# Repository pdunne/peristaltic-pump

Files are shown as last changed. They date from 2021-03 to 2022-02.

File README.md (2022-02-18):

# peristaltic-pump

Arduino code and electronics design for a simple peristaltic pump.

- Use a toggle switch to change between off, forward, and reverse flow
- A potentiometer to vary the rotation rate of the DC motor.
- Output the rotation direction and rotation rate as calibrated flow rate on a 128x64 OLED
- Can control two pumps simultaneously

## Getting Started

1. Wire all elements as shown in the diagram.
2. Ensure you have a recent version of the Adafruit SSD1306 library.
3. Use [I2C scanner](https://playground.arduino.cc/Main/I2cScanner/) to detect
the I2C address of your OLED (e.g. `0x3C`), and input it into the following line:
`display.begin(SSD1306_SWITCHCAPVCC, 0x3C);`
4. Compile and upload the program to your Arduino compatible board

> :warning: **WARNING: If you are using an old Adafruit library (before Nov. 2018)**:
> Find Adafruit_SSD1306.h under the Arduino libraries:
>
> `PATH_TO_ARDUINO_INSTALLATION/libraries/Adafruit_SSD1306/`
>
> Look for  `SSD1306 Displays` and uncomment one define to match your display:
>
> e.g. uncomment only `#define SSD1306_128_64` if using a 128x64 OLED
> That section of the file should look like:
>
>  ``` c
>/*=========================================================================
>    SSD1306 Displays
>    -----------------------------------------------------------------------
>    The driver is used in multiple displays (128x64, 128x32, etc.).
>    Select the appropriate display below to create an appropriately
>    sized framebuffer, etc.
>
>    SSD1306_128_64  128x64 pixel display
>
>    SSD1306_128_32  128x32 pixel display
>
>    SSD1306_96_16
>
>    -----------------------------------------------------------------------*/
>     #define SSD1306_128_64
>//   #define SSD1306_128_32
>//   #define SSD1306_96_16
>/*=========================================================================*/
> ```
>
> Additionally, in `pump_control.ino` you might need to comment out the following
> line:
>
> `Adafruit_SSD1306 display(SCREEN_WIDTH, SCREEN_HEIGHT, &Wire, OLED_RESET);`

## Needed Material

1. Arduino compatible board (Uno rev. 3 used for this example)
2. LM2596 DC-DC step down module
3. 12 V power adapter
4. DC barrel socket power jack
5. OLED 128x64 I2C Monochrome Display
6. Low powered peristaltic pump using 12 V DC motor
7. L293D H-Bridge motor driver
8. Rotary Potentiometer (e.g. 10 kΩ)
9. Single Pull Single Throw Toggle Switch (On-Off-On)

## Wiring Guide

bread board

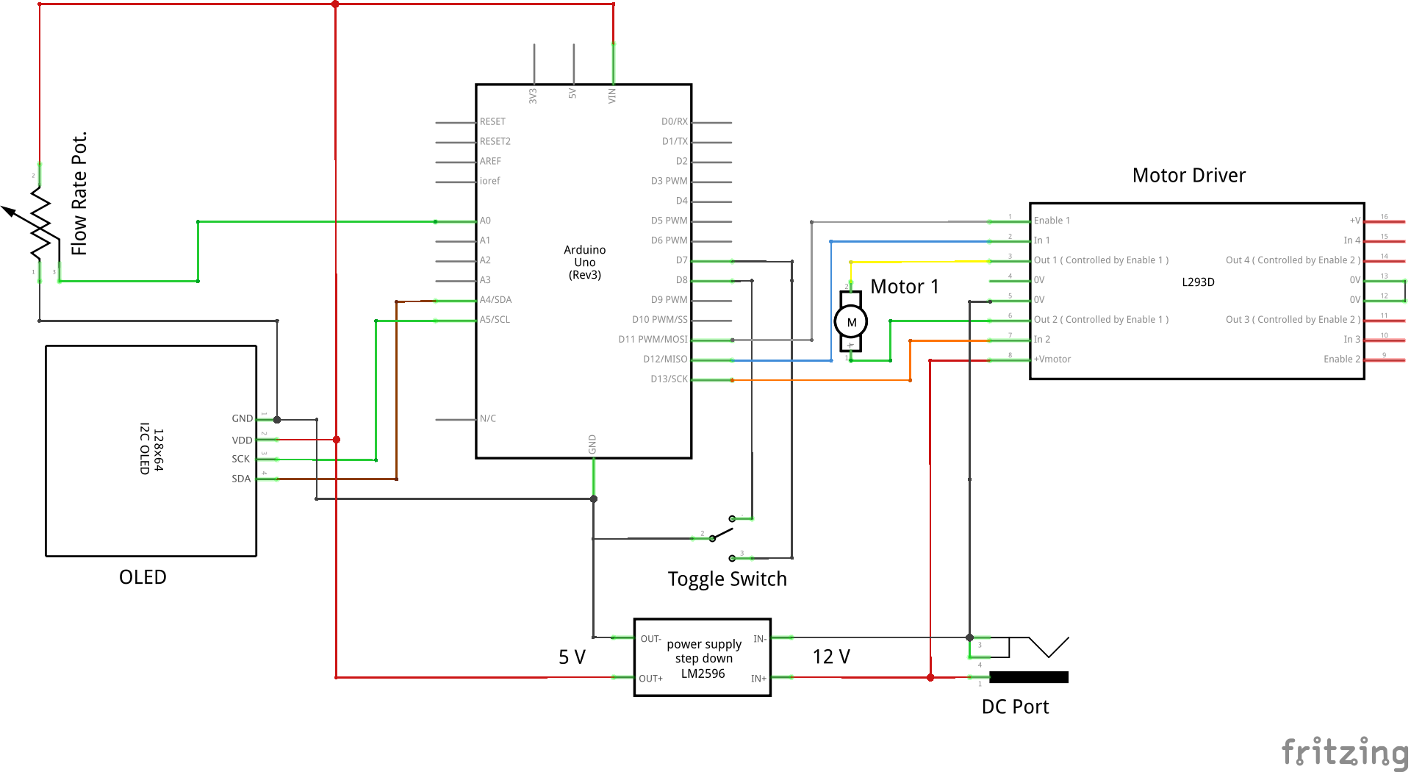
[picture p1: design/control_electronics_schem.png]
schematic


### Powering the Device

Assuming a 12 V DC adapter is used to power everything, it is convenient to place
a DC socket as the entry point to the device.
This be wired in two directions, the 12 V core to pin 8 of the L293D motor driver,
and to the high input of an LM2596 DC-DC step down converter. Similarly, the
ground can be connected to pin 3 of the L293D and the low input of the LM2596.
Adjust the DC-DC converter to produce 5 V across the output pins, which will be used
to drive the Arduino and OLED.

### Powering the Motor

We use control the motor in full H-bridge mode to be able to reverse the rotation
direction. Do this by connecting the following pins on the L293D motor driver:

| L293D              | Arduino/DC Jack     |
| ------------------ | ------------------- |
| Pin 1 (Enable)     | D11 PWM             |
| Pin 2 (In 1)       | D12                 |
| Pin 3 (Out 1)      | Motor pin 2         |
| Pin 4 (0 V )       | --                  |
| Pin 5 (0 V)        | Ground from DC Jack |
| Pin 6 (Out 2)      | Motor pin 1         |
| Pin 7 (In 2)       | D13                 |
| Pin 8 (+Vmotor)    | 12 V from DC Jack   |
| Pin 12 or 13 (0 V) | Ground from DC Jack |

Pins 2 and 7 determine the rotation state of the motor:

| Pin 2 | Pin 7 | Motor   |
| ----- | ----- | ------- |
| High  | Low   | Forward |
| Low   | High  | Reverse |
| High  | High  | Brake   |
| Low   | Low   | Brake   |

Pin 1 (Enable) is used to turn the motor, and regardless of pins 2 and 7, if Pin 1
(Enable) is low, then the motor will not rotate. Changing the rotation rate of the
motor is done using a PWM signal into Pin 1. This is sent as a duty cycle (% of
time on versus total time) as an int from 0 to 255 where 0%, i.e.  no pulses, and 255
means 100%, i.e. constant HIGH.

The function used to rotate the motor forward:

``` c
// Drives the motor forward at duty cycle 'duty_cycle'
void motor_forward(byte duty_cycle)
{
  display.println("Forward");
  digitalWrite(in1, HIGH);
  digitalWrite(in2, LOW);
  analogWrite(enable_motor_A, duty_cycle);
}
```

### Toggle Switch

The motor can be in one of three states, stopped, rotating forward, rotating reverse

Pins 7 and 8 are used for detecting the direction of a toggle switch (SPDT On-Off-On).
The two `On` poles of the switch are connected to pins 7 & 8, and the central pole
is connected to ground.

``` c
// Switch pins
const byte fwd_pin = 7; // Forward
const byte rev_pin = 8; // Reverse
```

We make sure the pins' internal pullup resistors are enabled to drive them to HIGH

```c
// Pins for Detecting Forward or Reverse
pinMode(fwd_pin, INPUT_PULLUP);
pinMode(rev_pin, INPUT_PULLUP);
```

Then whenever the toggle switch is enabled, this will ground one of the pins to LOW.
We detect the pin state with the following function, and then rotate or stop the
motor.

``` c
// Logic to check motor switch state
void motor_check()
{
  display.setCursor(0, 40);

  if (digitalRead(fwd_pin) == LOW)
  {
    motor_forward(duty_cycle);
  }
  else if (digitalRead(rev_pin) == LOW)
  {
    motor_reverse(duty_cycle);
  }
  else
  {
    motor_stop();
  }
}
```

### Flow Rate

The flow rate is set by reading the potential at pin `A0`,

`pot_value = analogRead(pot_read_pin);`

and mapping this to a value between 210-255. Lower than 210 stalls my motor

`duty_cycle = map(pot_value, 0, 1023, 210, 255);`

and for display on the OLED, the duty cycle is converted to flow rate calibrated
for this pump

```c
flow_rate = conv_flow_rate(duty_cycle);
```

The calibration was done using a third order polynomial, a balance between acurracy
and speed

```c
// Convert PWM values to flow rate. Only valid for forward flow, not reverse.
float conv_flow_rate(byte duty_cycle)
{
  // const float slope = 0.8073;
  // const float offset = -138.688;
  // float flow_rate = duty_cycle * slope + offset;

  // Third order polynomial.
  // Table lookup would be more efficient, but not needed
  const float a = -1.70373460e-04;
  const float b = 1.19023534e-01;
  const float c = -2.68600744e+01;
  const float d = 2.00133906e+03;
  float flow_rate = a * duty_cycle * duty_cycle * duty_cycle + b * duty_cycle * duty_cycle + c * duty_cycle + d;
  return flow_rate;
}
```

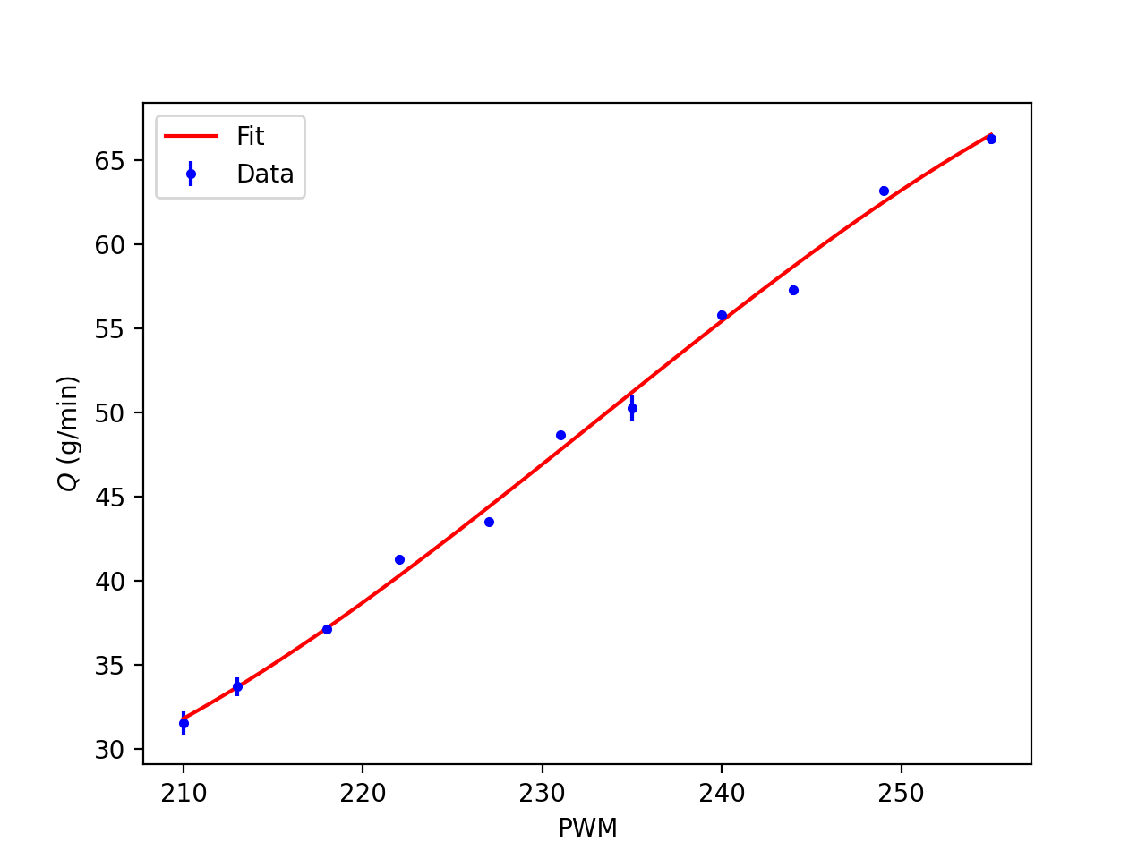
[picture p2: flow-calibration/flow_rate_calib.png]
calibration curve


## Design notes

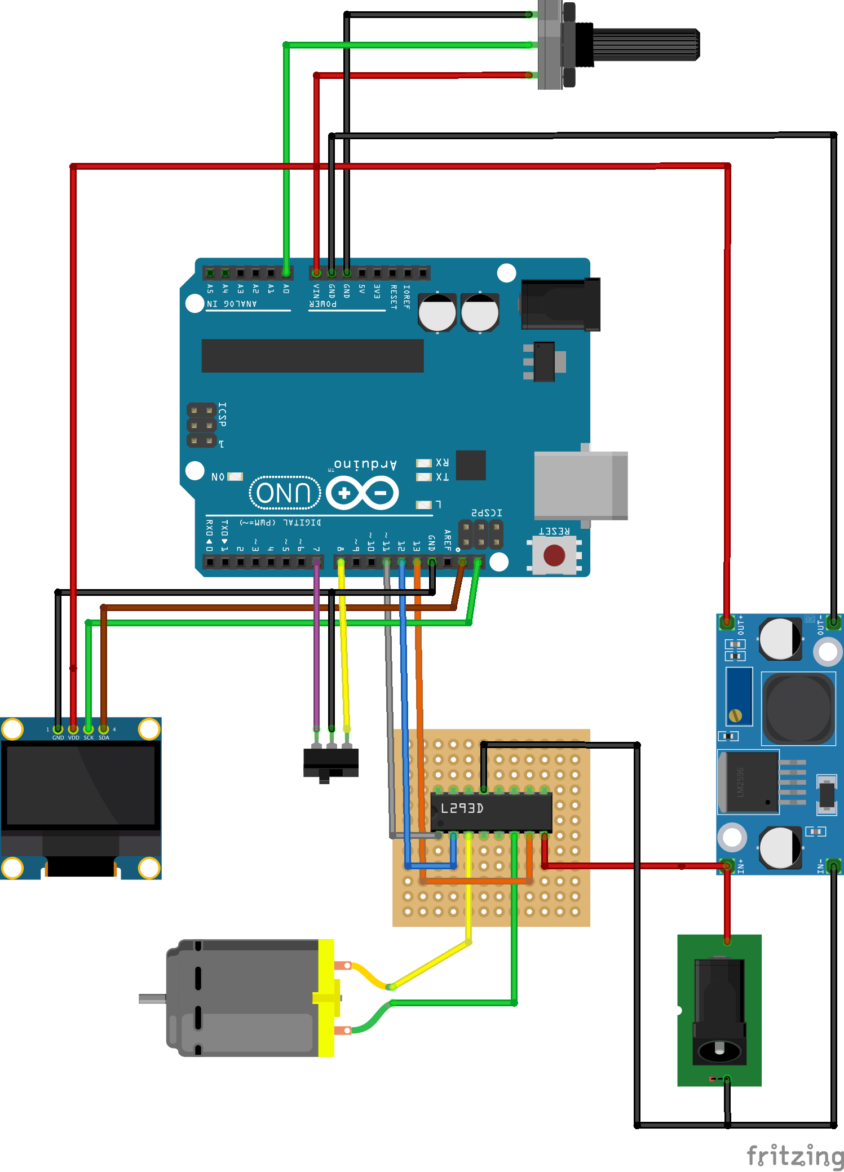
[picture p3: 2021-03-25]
design/control_electronics_bb.png

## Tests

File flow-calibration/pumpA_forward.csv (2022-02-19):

Duty Cycle | Flow | STD
100 | 72.77 | 0.174814187
90 | 67.4175 | 0.249537071
80 | 61.632 | 0.109799818
40 | 46.38 | 0.239930546
20 | 40.788 | 0.102254584
0 | 33.832 | 0.224267697

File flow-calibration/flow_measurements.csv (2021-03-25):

Dial | PWM | Run 1 | Run 2 | Run 3 | Run 4 | Run 5
0.0 | 210 | 29.276 | 30.750 | 31.311 | 31.880 | 32.340
0.5 | 213 | 32.569 | 32.906 | 33.880 | 34.097 | 33.997
1.0 | 218 | 34.444 | 37.031 | 36.854 | 37.268 | 37.479
1.5 | 222 | 41.044 | 41.140 | 41.052 | 41.264 | 41.697
2.0 | 227 | 42.368 | 43.372 | 43.759 | 43.458 | 43.476
2.5 | 231 | 48.790 | 48.511 | 48.486 | 48.824 | 48.823
3.0 | 235 | 49.093 | 50.091 | 50.013 | 49.673 | 51.343
3.5 | 240 | 56.028 | 55.395 | 55.812 | 55.972 | 55.943
4.0 | 244 | 56.519 | 57.570 | 57.165 | 56.925 | 57.457
4.5 | 249 | 63.440 | 63.283 | 63.025 | 63.467 | 62.915
5.0 | 255 | 65.555 | 66.437 | 66.642 | 65.954 | 66.056

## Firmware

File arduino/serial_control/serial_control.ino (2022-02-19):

/* This Source Code Form is subject to the terms of the Mozilla Public
 * License, v. 2.0. If a copy of the MPL was not distributed with this
 * file, You can obtain one at https://mozilla.org/MPL/2.0/.
 * Copyright 2022 Peter Dunne
 */

/*
Peristaltic Pump Control

Serial control of two DC pumps simultaneously.
Output the rotation direction and rotation rate as calibrated flow rate on a
128x64 OLED

Updated Feb 2022
By Peter Dunne

https://www.applied-magnetism.com/
https://github.com/pdunne/peristaltic-pump
*/

#include <SPI.h>
#include <Wire.h>
#include <Adafruit_SSD1306.h>

#define SCREEN_WIDTH 128 // OLED display width, in pixels
#define SCREEN_HEIGHT 64 // OLED display height, in pixels

// Declaration for an SSD1306 display connected to I2C (SDA, SCL pins)
#define OLED_RESET -1 // Reset pin # (or -1 if sharing Arduino reset pin)

/* New way to define screen properties with SSD1306 library. Might need to be
commented out for older versions of header. */
Adafruit_SSD1306 display(SCREEN_WIDTH, SCREEN_HEIGHT, &Wire, OLED_RESET);

const int loop_delay = 100; // Loop delay in ms

// Defines control pins, and min and max PWM values for a DC motor
struct Motor
{
  byte enable; // Enable motor (Digital pin)
  byte pin1;   // Input 1 (Digital pin)
  byte pin2;   // Input 2 (Digital pin)
  byte minPWM; // Minimum PWM duty cycle
  byte maxPWM; // Maximum PWM duty cycle
  byte id;     // Pump ID
};

// Defines forward and reverse detection pins
struct Control
{
  const byte fwd; // Forward Pin (Digital)
  const byte rev; // Reverse Pin (Digital)
  const byte pot; // Potentiometer Pin (Analog)
  byte flag;      // Status flag 0 - off, 1 - forward, 2 - reverse
};

// Stores potentiometer reading, duty cycle %, and calibrated flow rate in l/min
struct Flow
{
  int potVal;     // Potentiometer value
  byte dutyCycle; // Mapped duty cycle
  float flowRate; // Flow rate in l/min
};

typedef struct Motor Motor;
typedef struct Control Control;
typedef struct Flow Flow;

// Motor connections on H-Bridge
Motor motA = {11, 12, 13, 170, 255, 0};
Motor motB = {5, 4, 2, 180, 255, 1};

// Direction control pins
Control controlA = {7, 8, 0, 0};
Control controlB = {0, 1, 1, 0};

Flow flowA = {0, 0, 0.0};
Flow flowB = {0, 0, 0.0};

/******************************************/

// Function Prototypes
void setup(void);
void loop(void);
void init_switch(Control *control);
void init_motor(const Motor *motor);
void off_motor(const Motor *motor);
void motor_stop(const Motor *motor);
void motor_forward(const Motor *motor, byte dutyCycle);
void motor_reverse(const Motor *motor, byte dutyCycle);
void motor_check(const Motor *motor, Control *control, byte dutyCycle);
void init_display(byte dutyCycle);
void print_flow_rate(float flow_rate);
float conv_flow_rate(byte dutyCycle);
void control_flow(Motor *motor, Control *control, Flow *flow);

/******************************************/

// Setup board
void setup()
{
  // Set all the motor control pins to outputs
  init_motor(&motA);
  init_motor(&motB);

  // Turn off motor - Initial state
  off_motor(&motA);
  off_motor(&motB);

  // Pins for Detecting Forward or Reverse
  init_switch(&controlA);
  init_switch(&controlB);

  // Serial.begin(9600);
  // Set the address of the OLED
  display.begin(SSD1306_SWITCHCAPVCC, 0x3C);

  // Clear the buffer.
  display.clearDisplay();

  // Display Text
  display.setTextSize(3);
  display.setTextColor(WHITE);
  display.setCursor(0, 0);

  display.display();
  display.clearDisplay();
}
/******************************************/

// Detection of pins and control of pumps
void loop()
{
  // Reads potentiometer and sets the flow rate
  control_flow(&motA, &controlA, &flowA);
  control_flow(&motB, &controlB, &flowB);

  // Initialise display
  init_display(flowA.dutyCycle);

  // Check motor and display status
  display.setCursor(0, 40);

  motor_check(&motA, &controlA, flowA.dutyCycle);
  // display.setCursor(20, 40);
  motor_check(&motB, &controlB, flowB.dutyCycle);

  // Display Flow rate
  // print_flow_rate(flowA.flowRate);
  // print_flow_rate(flowB.flowRate);

  display.display();
  delay(loop_delay);
}

// Initialises pullup pins for switch detection
void init_switch(Control *control)
{
  pinMode(control->fwd, INPUT_PULLUP);
  pinMode(control->rev, INPUT_PULLUP);
}

// Intialises pins for controlling a motor
void init_motor(const Motor *motor)
{
  pinMode(motor->enable, OUTPUT);
  pinMode(motor->pin1, OUTPUT);
  pinMode(motor->pin2, OUTPUT);
  digitalWrite(motor->enable, LOW);
}

// Turns off a motor
void off_motor(const Motor *motor)
{
  digitalWrite(motor->pin1, LOW);
  digitalWrite(motor->pin2, LOW);
  analogWrite(motor->enable, 0);
}

// Turns off a motor
void motor_stop(const Motor *motor)
{
  display.println("Off");
  off_motor(motor);
}

// Drives the motor forward at duty cycle 'dutyCycle'
void motor_forward(const Motor *motor, byte dutyCycle)
{
  display.println("Forward");
  digitalWrite(motor->pin1, HIGH);
  digitalWrite(motor->pin2, LOW);
  analogWrite(motor->enable, dutyCycle);
}

// Drives the motor in reverse at duty cycle 'dutyCycle'
void motor_reverse(const Motor *motor, byte dutyCycle)
{
  display.println("Reverse");
  digitalWrite(motor->pin1, LOW);
  digitalWrite(motor->pin2, HIGH);
  analogWrite(motor->enable, dutyCycle);
}

// Logic to check motor switch state
void motor_check(const Motor *motor, Control *control, byte dutyCycle)
{

  if (digitalRead(control->fwd) == LOW)
  {
    control->flag = 1;
    motor_forward(motor, dutyCycle);
  }
  else if (digitalRead(control->rev) == LOW)
  {
    control->flag = 2;
    motor_reverse(motor, dutyCycle);
  }
  else
  {
    control->flag = 0;
    motor_stop(motor);
  }
}

// Initialise display
void init_display(byte dutyCycle)
{
  display.clearDisplay();
  display.setTextColor(WHITE);
  display.setCursor(0, 0);
  display.setTextSize(1);
  display.print("Motor:");
  display.setCursor(64, 0);
  display.println("Flow Rate:");
  display.setTextSize(2);
  // display.print(map(dutyCycle, min_PWM, max_PWM, 0, 100), DEC);
  display.print(flowA.dutyCycle);
  display.print(flowB.dutyCycle);

  // display.println("%");
}

// Display flow rate on OLED
void print_flow_rate(float flow_rate)
{
  display.setCursor(64, 8);
  display.println(flow_rate, 1);
  display.setCursor(64, 24);
  display.print("ml/mn");
}

// Convert PWM values to flow rate. Only valid for forward flow, not reverse.
float conv_flow_rate(byte dutyCycle)
{
  // const float slope = 0.8073;
  // const float offset = -138.688;
  // float flow_rate = dutyCycle * slope + offset;

  // Third order polynomial.
  // Table lookup would be more efficient, but not needed
  const float a = -1.70373460e-04;
  const float b = 1.19023534e-01;
  const float c = -2.68600744e+01;
  const float d = 2.00133906e+03;
  float flow_rate = a * dutyCycle * dutyCycle * dutyCycle + b * dutyCycle * dutyCycle + c * dutyCycle + d;
  return flow_rate;
}

void control_flow(Motor *motor, Control *control, Flow *flow)
{
  // Read the potentiometer
  flow->potVal = analogRead(control->pot);

  // Map analogue read to from motor.minPWM to motor.maxPWM lower than this stalls the motor
  flow->dutyCycle = map(flow->potVal, 0, 1023, motor->minPWM, motor->maxPWM);

  // Calculate the calibrated flow rate
  flow->flowRate = conv_flow_rate(flow->dutyCycle);
}
/*******************************************/

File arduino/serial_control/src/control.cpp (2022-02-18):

#include <Arduino.h>
#include "control.h"

//TODO: Dummy variables, need to be measured and updated
Calib fwdA = {0.0, 0.0, 0.8, -133.0};
Calib revA = {0.0, 0.0, 0.81, -139.0};
Calib fwdB = {0.0, 0.0, 0.82, -135.0};
Calib revB = {0.0, 0.0, 0.8, -132.0};

// Initialises pullup pins for switch detection
void init_switch(Control *control)
{
    pinMode(control->fwd, INPUT_PULLUP);
    pinMode(control->rev, INPUT_PULLUP);
}

// Intialises pins for controlling a motor
void init_motor(const Motor *motor)
{
    pinMode(motor->enable, OUTPUT);
    pinMode(motor->pin1, OUTPUT);
    pinMode(motor->pin2, OUTPUT);
    digitalWrite(motor->enable, LOW);
}

// Turns off a motor
void off_motor(const Motor *motor)
{
    digitalWrite(motor->pin1, LOW);
    digitalWrite(motor->pin2, LOW);
    analogWrite(motor->enable, 0);
}

// Convert PWM values to flow rate, depending on motor type and direction
float conv_flow_rate(byte dutyCycle, byte flag, byte id)
{

    if (id == 1)
    {
        if (flag == 2)
        {
            return get_flow_rate(dutyCycle, &revB);
        }
        else
        {
            return get_flow_rate(dutyCycle, &fwdB);
        }
    }

    else
    {
        if (flag == 2)
        {
            return get_flow_rate(dutyCycle, &revA);
        }
        else
        {
            return get_flow_rate(dutyCycle, &fwdB);
        }
    }
}

// Converts dutyCycle to calibrated flow rate
float get_flow_rate(byte dutyCycle, Calib *calib)
{
    // Third order polynomial.
    // Table lookup would be more efficient, but not needed

    float flow_rate = ((calib->a) * dutyCycle * dutyCycle * dutyCycle) + ((calib->b) * dutyCycle * dutyCycle) + ((calib->c) * dutyCycle) + (calib->d);
    return flow_rate;
}

// Reads control potentiometer and generates duty cycle and flow rate
void control_flow(Assem *assem)
{
    // Read the potentiometer
    assem->flow->potVal = analogRead(assem->control->pot);

    // Map analogue read to from motor.minPWM to motor.maxPWM lower than this stalls the motor
    assem->flow->dutyCycle = map(assem->flow->potVal, 0, 1023, assem->motor->minPWM, assem->motor->maxPWM);

    // Calculate the calibrated flow rate
    assem->flow->flowRate = conv_flow_rate(assem->flow->dutyCycle, assem->control->flag, assem->motor->id);
}

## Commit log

2021-03-25 First Documentation
    Example files and documentation
    [control_electronics.fzz, flow_measurements.csv, flow_meter.fzz]
2022-02-18 BREAKING CHANGE: Control of two motors
    Major rearrangement of code
    Separation of pump control and display into header files.
2022-02-19 feat: first calibrations
    fix: display PWM during timed loop control
    [pumpA_forward.csv, pumpA_forward_raw.csv, pumpB_forward.csv]
2022-02-21 feat: calibrated flow rates
    feat: timed routine
    For a timed routine, the pump will run for 60s and then stop.
